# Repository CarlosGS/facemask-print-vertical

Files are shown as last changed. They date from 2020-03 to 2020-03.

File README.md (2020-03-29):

# facemask-print-vertical

Designs available:

- Stacked: Prusa mask main part

- Stacked: Protective visor by 3dverkstan

- The A mask homologated in a hospital in Madrid (unfortunately I cannot recommend the design, simpler is better, so avoid this one)
  - Original B1 part
  - Stacked: B2 part

There is one empty layer between each part to allow an easy separation. Support material not needed.

Hay una capa vacía entre cada pieza, lo que permite separarlas fácilmente. No es necesario material de soporte.

## Check the Z layers before printing to ensure there is exactly one layer missing between each part

## First adjust your setup with the calibration example:

https://github.com/CarlosGS/facemask-print-vertical/tree/master/source_code/adhesion_test

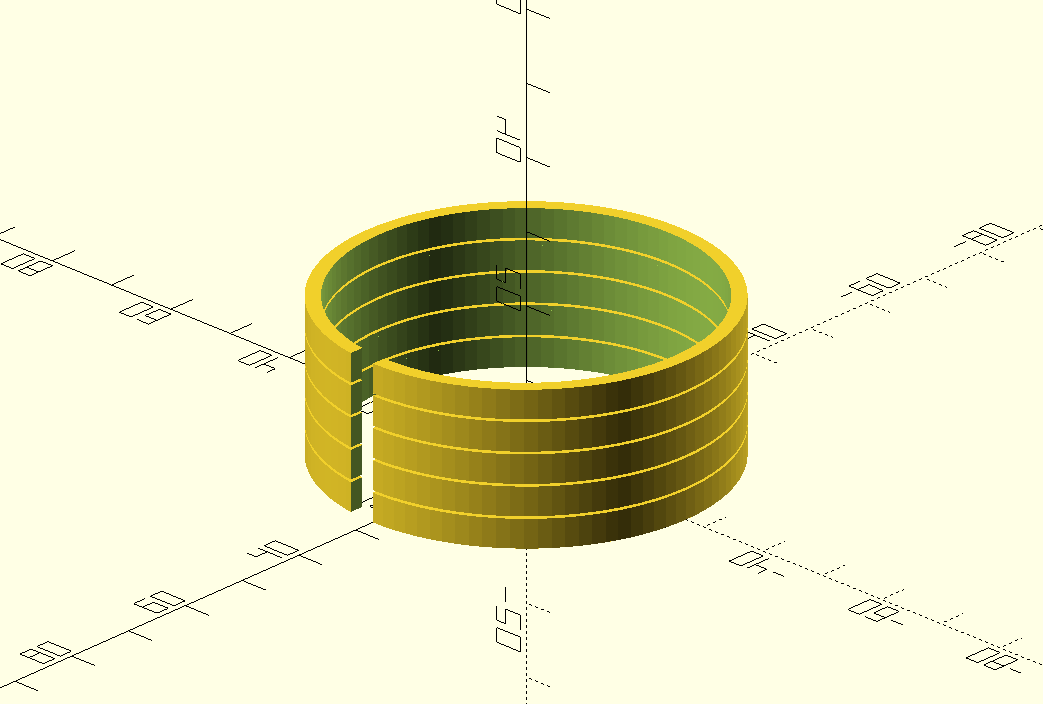
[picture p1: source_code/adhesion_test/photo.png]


**Always check the generated layers before printing!!**

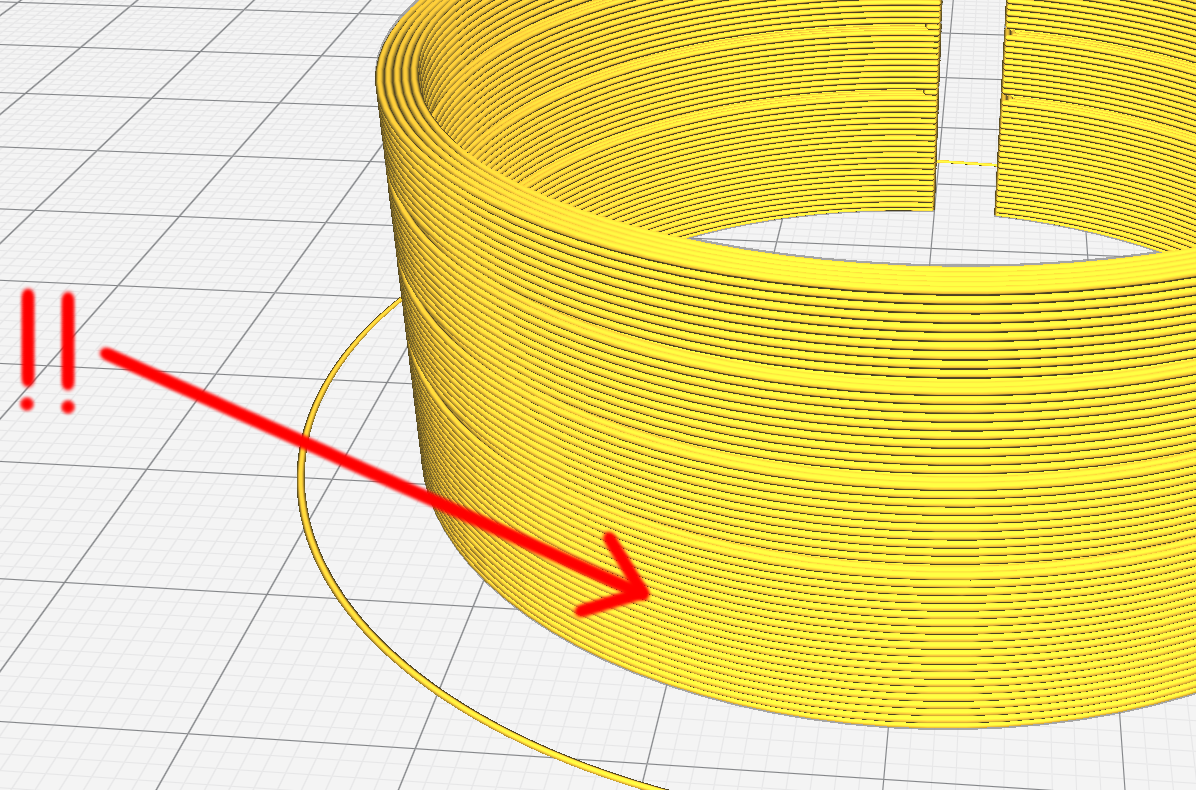
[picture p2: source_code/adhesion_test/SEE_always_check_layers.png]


Tested with [this cura profile](https://github.com/MKme/I3-Mega-3D-Printer-Settings-Resources/blob/master/Cura%20Profiles/i3%20Mega%20Erics%20Main%20Profile.curaprofile) (see [the result](https://twitter.com/MKmeOrg/status/1243522985262186496) ). I suggest to **first try with your own profile** and then adjust layer height.

## Please open an issue if you have any requests

Stacked with OpenScad software, the code is available in the "source_code" directory.

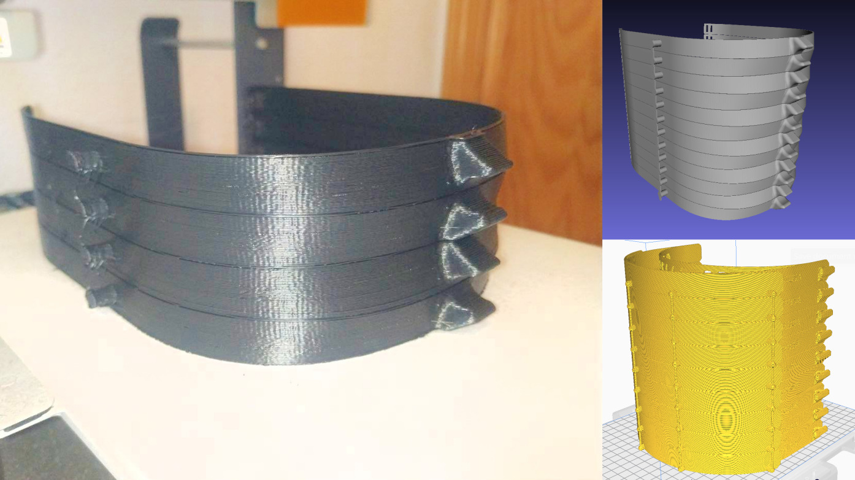
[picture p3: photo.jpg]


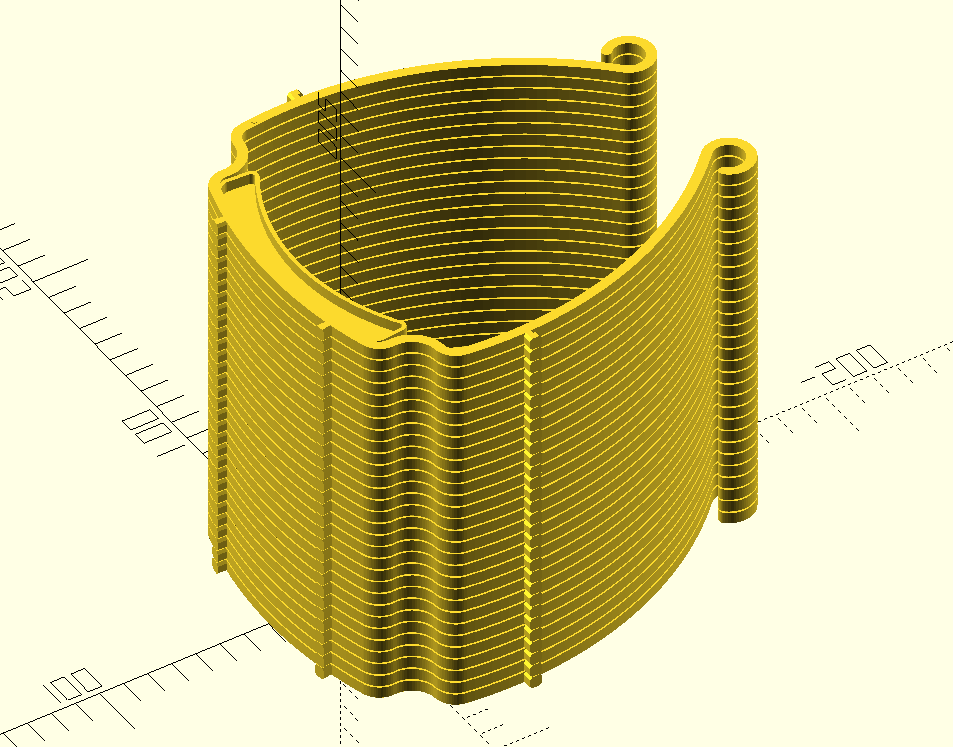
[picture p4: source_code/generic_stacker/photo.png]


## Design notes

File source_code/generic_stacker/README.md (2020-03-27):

# Stack and print multiple copies (easy separation!)

Tutorial to generate your own models:

- They need to be flat on top and bottom
- Open the stack.scad file using https://www.openscad.org/
- Edit the variables (model thickness, separation, etc)
- Compile the model using F5 to preview until all looks OK
- Render with F6 and export the STL file.

Tested with [this cura profile](https://github.com/MKme/I3-Mega-3D-Printer-Settings-Resources/blob/master/Cura%20Profiles/i3%20Mega%20Erics%20Main%20Profile.curaprofile) (see [the result](https://twitter.com/MKmeOrg/status/1243522985262186496) ). I suggest to **first try with your own profile and layer height 0.3mm**. Normally there is NO need for support material.

## Check the Z layers before printing to ensure there is exactly one layer missing between each part

## First adjust your setup with the calibration example:

https://github.com/CarlosGS/facemask-print-vertical/tree/master/source_code/adhesion_test



#### The example used is https://3dverkstan.se/protective-visor/ by 3dverkstan. More files are [here](https://github.com/CarlosGS/facemask-print-vertical/tree/master/stl)



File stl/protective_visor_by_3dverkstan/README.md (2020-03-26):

Files here generated from: https://3dverkstan.se/protective-visor/ 

OpenScad script and instructions: https://github.com/CarlosGS/facemask-print-vertical/tree/master/source_code/generic_stacker

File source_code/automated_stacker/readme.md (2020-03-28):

# Description
    This tool is for people who wants to enable people who does not have openscad.
    Some folk with 3D printers may want to print different numbers of copies without the hassle of 
    touching .scad files.
# Requirements:
- The stacker.scad should have a variable named N_COPIES that defines the number of copies.
- Openscad file need to be in the same directory as the makefile.
- Openscad file needs to correctly reference the path to the stl file.
- The folder structured would look something like:

    ├── 3dverkstan_stacker.scad

    ├── makefile

    ├── readme.md

    └── Visor_frame_EUROPE_ISO838_v3.stl

- A folder named 'nameofmystacker_stls' will be created to store the generated stl files.

example of usage to generate stl files with 1 to 20 stacked visors:

    make stacker=stack_model.scad N_COPIES=20

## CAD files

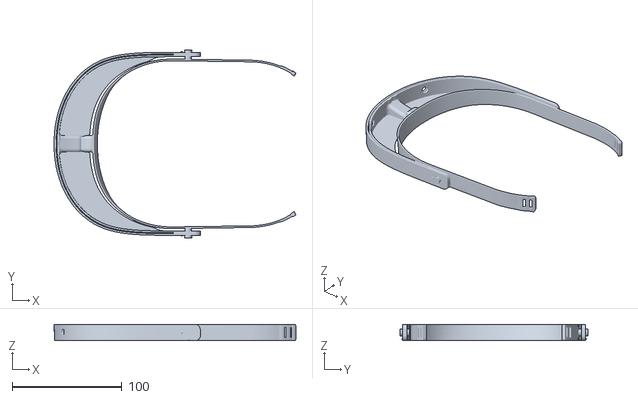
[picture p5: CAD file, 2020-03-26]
source_code/A -Principal Visera Madrid-Aprobada 1.0.stl
220.0 x 171.2 x 15.0

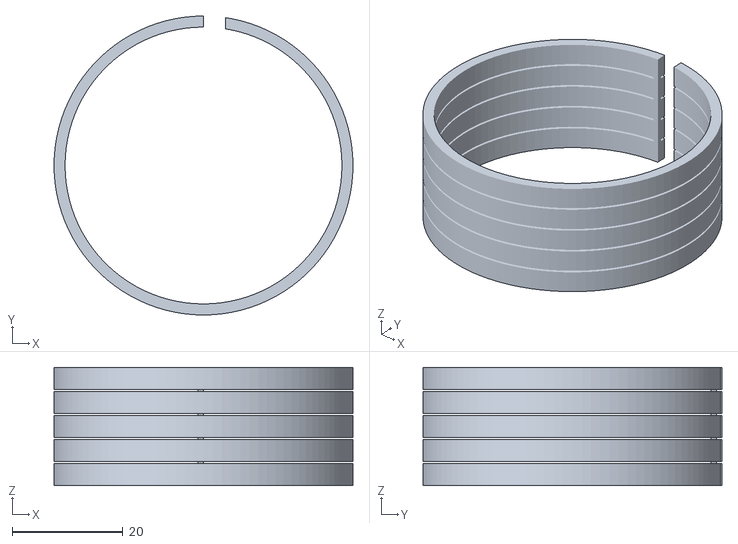
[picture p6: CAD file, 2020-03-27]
source_code/adhesion_test/adhesion_test.stl
54.0 x 54.0 x 21.4

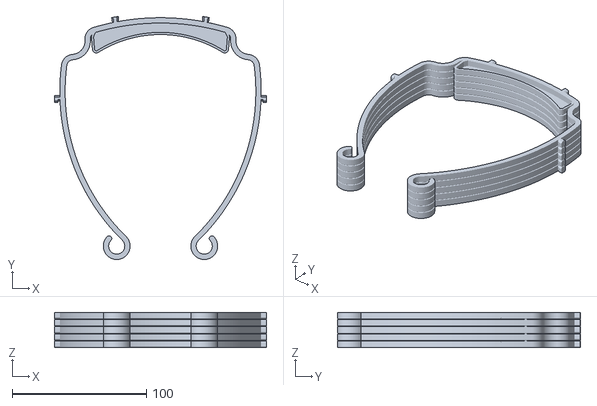
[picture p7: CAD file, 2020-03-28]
source_code/automated_stacker/3dverkstan_stacker.scad_stls/stacked_5.stl
158.0 x 181.0 x 26.4

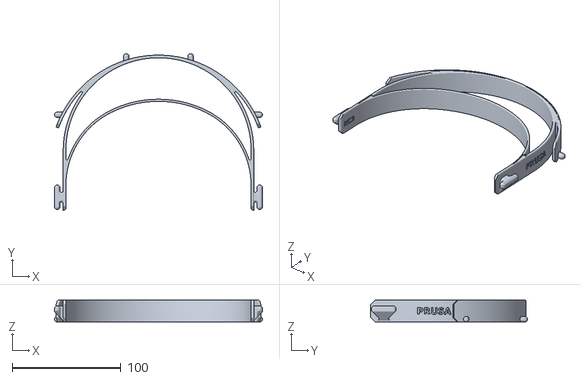
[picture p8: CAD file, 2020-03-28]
source_code/automated_stacker/prusa_stacker.scad_stls/stacked_1.stl
191.0 x 143.8 x 20.0

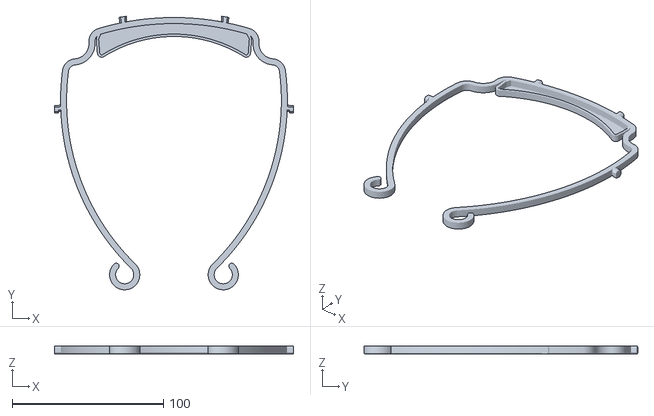
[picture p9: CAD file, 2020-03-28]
source_code/automated_stacker/Visor_frame_EUROPE_ISO838_v3.stl
158.0 x 181.0 x 5.00

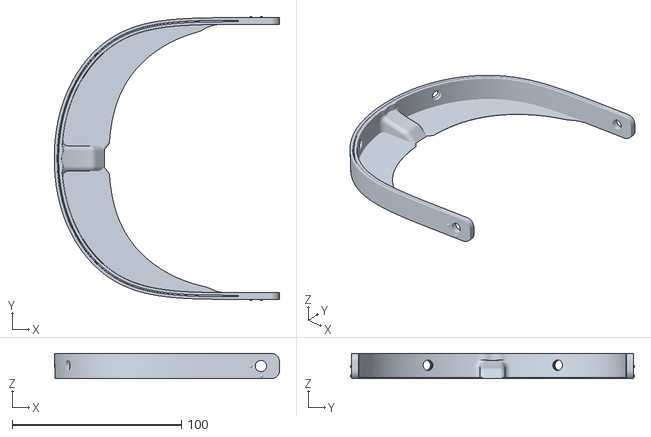
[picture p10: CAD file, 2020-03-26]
stl/B1 Visera Madrid-Aprobada 1.0.stl
133.2 x 167.8 x 15.0

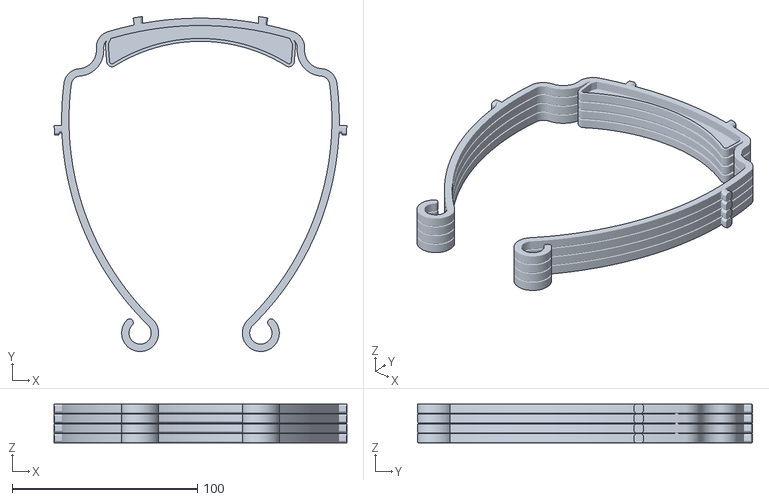
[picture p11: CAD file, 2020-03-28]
source_code/automated_stacker/3dverkstan_stacker.scad_stls/stacked_4.stl
158.0 x 181.0 x 21.1

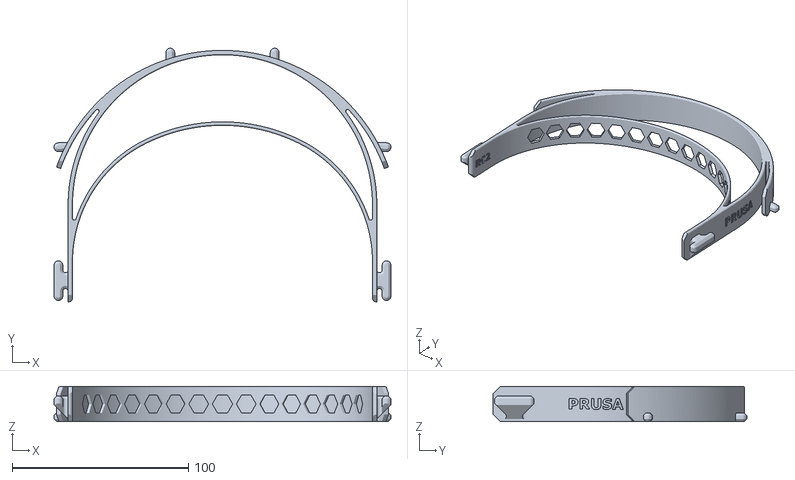
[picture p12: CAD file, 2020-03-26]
source_code/automated_stacker/covid19_headband_rc2.stl
191.0 x 143.8 x 20.0

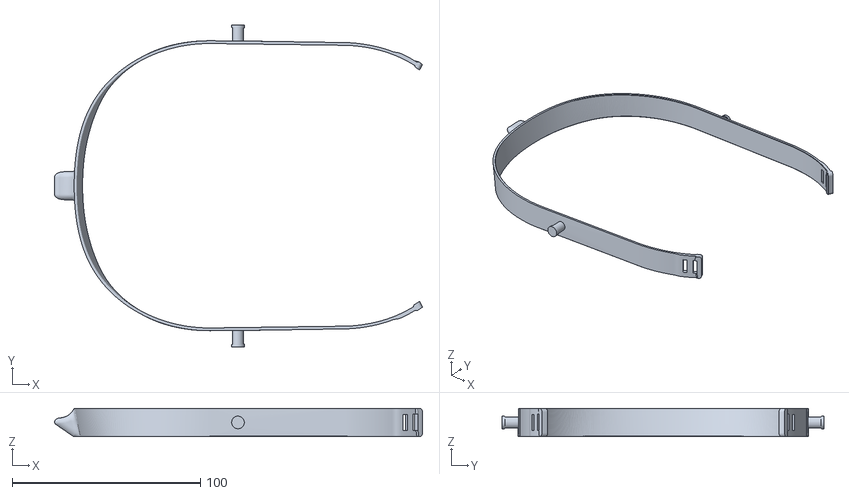
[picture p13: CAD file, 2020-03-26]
source_code/B2 Visera Madrid-Aprobada 1.0.stl
195.5 x 171.2 x 15.0

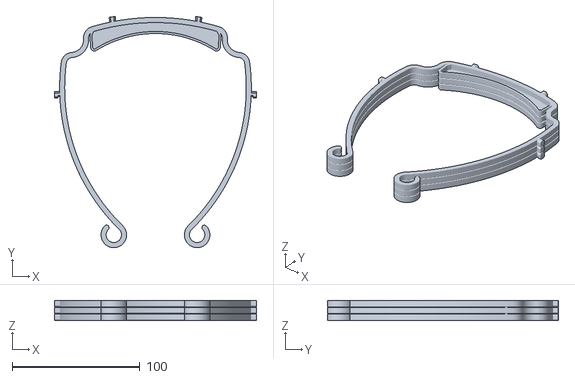
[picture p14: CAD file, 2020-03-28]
source_code/automated_stacker/3dverkstan_stacker.scad_stls/stacked_3.stl
158.0 x 181.0 x 15.7

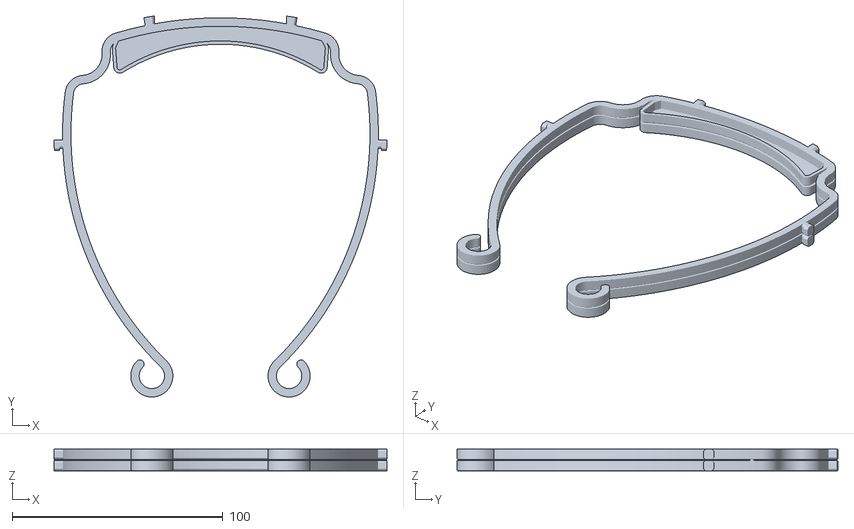
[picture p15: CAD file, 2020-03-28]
source_code/automated_stacker/3dverkstan_stacker.scad_stls/stacked_2.stl
158.0 x 181.0 x 10.3

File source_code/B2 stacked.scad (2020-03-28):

// Variables
number_of_parts=6;

// Additional supports
translate([89.3,84.3,-6.74])
cube([3,1.2,14*(number_of_parts)]);

translate([89.3,-85.5,-6.74])
cube([3,1.2,14*(number_of_parts)]);


// Generation
for (i = [0:number_of_parts-1])
    translate([0,0,i*(13.5+0.35)])
    rotate([i*180,0,0])
    render()
    translate([72,-13.86,-15/2-0.25])
    difference() {
        import("B2 Visera Madrid-Aprobada 1.0.stl");
        cube([300,300,2],center=true);
        translate([0,0,15])
        cube([300,300,1],center=true);
    }

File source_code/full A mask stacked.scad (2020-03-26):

translate([89.3,84.3,-6.74])
cube([3,1.2,160]);

translate([89.3,-85.5,-6.74])
cube([3,1.2,160]);

for (i = [0:11])
 translate([0,0,i*(13.5+0.35)])
rotate([i*180,0,0]) render()
translate([72,-13.86,-15/2-0.25])
difference() {
import("A -Principal Visera Madrid-Aprobada 1.0.stl");
cube([300,300,2],center=true);
translate([0,0,15])
cube([300,300,1],center=true);
}

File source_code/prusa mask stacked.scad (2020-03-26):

for(i=[-1,1]) {
translate([i*93,22.85,-8])
cylinder(r=1,h=163,$fn=16);

translate([i*29.55,76.5,-8])
cylinder(r=1,h=163,$fn=16);

}

for (i = [0:8])
 translate([0,0,i*(20+0.35)])
translate([-844.5,0,0])
import("covid19_headband_rc2.stl");

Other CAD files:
source_code/automated_stacker/3dverkstan_stacker.scad_stls/stacked_1.stl
source_code/adhesion_test/adhesion_test.scad
source_code/adhesion_test/adhestion_test.scad
source_code/automated_stacker/3dverkstan_stacker.scad
source_code/automated_stacker/prusa_stacker.scad
stl/PANTALLA_SACYL/generador.scad

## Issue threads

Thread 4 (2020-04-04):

### ISSUE TITLE
Solicitud de modelo

### ISSUE THREAD

**Issue by theotocopulitos** [CarlosGS/facemask-print-vertical#4]
¿Se puede generar un modelo apilable del adjunto? (es el "oficial" de Castilla y León)
[PANTALLA_SACYL_3.1.zip](https://github.com/CarlosGS/facemask-print-vertical/files/4431765/PANTALLA_SACYL_3.1.zip)

**Comment by CarlosGS** [comment]
Añadido, dime si lo consigues!! :)
https://github.com/CarlosGS/facemask-print-vertical/tree/master/stl/PANTALLA_SACYL

**Comment by theotocopulitos** [comment]
Carlos,

Mil gracias. Esta noche he probado la de 5, y perfecto... se separan
bien... todo genial. Me ha salido mal, curiosamente, la 4ª, pero las de
abajo y las de arriba perfectas... en cuanto ajuste un poco los parámetros,
a tope.

Muchas gracias, has mejorado infinitamente la calidad de mi sueño...

Arturo

**Comment by CarlosGS** [comment]
Bieeen :-)
Pasa foto del resultado para ver qué pudo pasar. Utilizas Cura?

**Comment by theotocopulitos** [comment]
De las otras dos quedaron muy bien y dos utilizables con un poco de lija previa. Esta no recuerdo si es la 3 o 4. 

Sí uso Cura

**Comment by CarlosGS** [comment]
Vaya, no se ha mandado! Prueba a adjuntarla desde la web de github mejor. Si puedes saca foto de la pila completa. Gracias!!

**Comment by theotocopulitos** [comment]
A ver si así las ves... no tengo fotos del pack.

Tengo de tres, y la que salió mal... La de abajo salió perfecta. Parece como que al empezar cada nueva pieza hay retracción y se mete un poco el arco...a partir de la 3ª o 4ª capas superiores se coloca bien... salvo en la que quedó mal que ese efecto pilló muchas más capas y fue mucho más acusado.

![unnamed (1)](https://user-images.githubusercontent.com/1540135/78505605-db74d480-7774-11ea-8567-c5508576835a.jpg)
![unnamed](https://user-images.githubusercontent.com/1540135/78505606-dca60180-7774-11ea-9c24-bf719040724e.jpg)
![IMG_8255](https://user-images.githubusercontent.com/1540135/78505608-de6fc500-7774-11ea-9216-183070bb38ed.JPG)

**Comment by theotocopulitos** [comment]
No me di cuenta de usar tu perfil... sí verifiqué capas vacías, pero me olvidé del perfil que pones

**Comment by CarlosGS** [comment]
Gracias! Ya veo!
El perfil lo saqué de aquí: https://twitter.com/MKmeOrg/status/1243522985262186496

Yo no me molestaría en cambiarlo, creo que el problema está relacionado con el bisel que tienen algunas máscaras en la base:
![Screenshot_20200405_194647](https://user-images.githubusercontent.com/1636266/78505834-5c809b80-7776-11ea-9287-1fc7c83ed0bf.png)

**Comment by theotocopulitos** [comment]
Vaya...

también veo que ses perfil tiene espesor de capa 0.2... el mío 0.3... no creo que influya, pero...

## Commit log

2020-03-26 Create B2 stacked.scad
    [B2 stacked.scad]
2020-03-28 Coded improved with a parameter variable and some comments for clearance
    [B2 stacked.scad]
2020-03-28 Automate stl generation using stackers.scad
    [3dverkstan_stacker.scad, Visor_frame_EUROPE_ISO838_v3.stl, stacked_1.stl, stacked_2.stl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]
2020-03-28 stacked stls for prusa's face mask
    [covid19_headband_rc2.stl, prusa_stacker.scad, stacked_1.stl]
